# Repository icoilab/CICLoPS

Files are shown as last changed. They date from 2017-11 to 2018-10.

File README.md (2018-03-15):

# CICLoPS Photometry Project
Open source in-vivo fiber photometry for low-light level recordings

# Background
Fiber photometry is a tool used in neuroscience to optically monitor neural correlates of behavior to targeted neuronal populations in the brain. When applied to study neurons genetically-targeted to express optical reporters of local physiological dynamics, the experimentalist gains access to real-time activity of arbitrary neuronal populations during behavioral assays. 

The technology surrounding photometry has matured rapidly, and multiple systems have been reported and several solutions are now commercially available. However, mainstream technologies have limitations, of which poor sensitivity to fluorescence is a notable challenge. This problem is compensated in experiments by increasing the level of input excitation light. However, this causes increased destruction of the fluorescent proteins, which results in a reduction in overall brightness, and largely restricts studies to short-term transients, precluding longer-term and repeated investigations into optically-reported neuronal activity. The [Integrated Circuits and Optical Imaging Laboratory](http://people.ucalgary.ca/~kmurari/index.html) at the University of Calgary developed a high-performance, cost-effective system for deep-brain optical measurements of fluorescence intensity transients in freely-moving animals that achieves excellent Signal-to-noise ratio at extremely low levels of input excitation light. The system is named CICLoPS for **C**ost-effective, ***I**n-Vivo*, **C**ustomizeable, **Lo**w-Power, **P**hotometry **S**ystem.

# Components
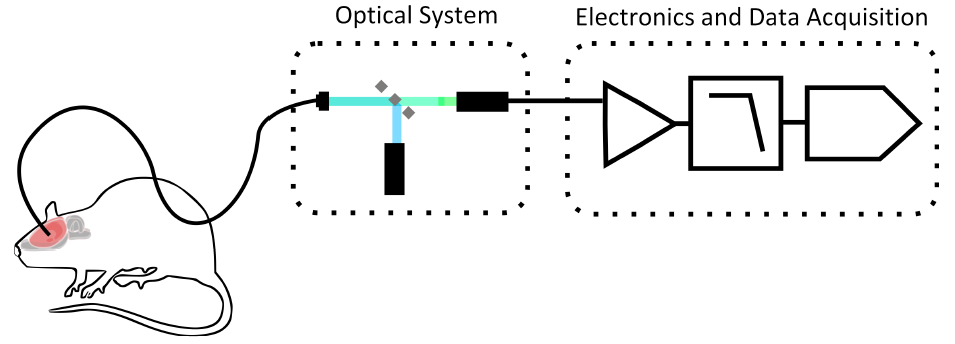
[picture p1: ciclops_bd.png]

CICLoPS is a complete solution for in-vivo fiber photometry, designed specifically to monitor neural activity with low-light levels. The Construction and Assembly Guide for the [core system](../../tree/master/ciclops-core "ciclops-core") refers to source files in the [optical system](../../tree/master/ciclops-core/optics "optics"), [coherent detection hardware](../../tree/master/ciclops-core/electronics "electronics"), and [code for data acquisition](../../tree/master/ciclops-core/acquisition "acquisition"). Instructions on how to achieve [additional functions](../../tree/2x-artifact) are also provided.

# Related Work
This development builds on the prior contributions from several others, listed below.

[1] Grienberger, Christine, et al. "Sound‐evoked network calcium transients in mouse auditory cortex in vivo." The Journal of physiology 590.4 (2012): 899-918.

[2] Cui, Guohong, et al. "Deep brain optical measurements of cell type–specific neural activity in behaving mice." Nature protocols 9.6 (2014): 1213.

[3] Gunaydin, Lisa A., et al. "Natural neural projection dynamics underlying social behavior." Cell 157.7 (2014): 1535-1551.

[4] LeChasseur, Yoan, et al. "A microprobe for parallel optical and electrical recordings from single neurons in vivo." Nature methods 8.4 (2011): 319-325.

[5] Lerner, Talia N., et al. "Intact-brain analyses reveal distinct information carried by SNc dopamine subcircuits." Cell 162.3 (2015): 635-647.

[6] Kim, Christina K., et al. "Simultaneous fast measurement of circuit dynamics at multiple sites across the mammalian brain." Nature 201 (2016): 6.

[7] Pashaie, Ramin, and Ryan Falk. "Single optical fiber probe for fluorescence detection and optogenetic stimulation." IEEE Transactions on Biomedical Engineering 60.2 (2013): 268-280.

[8] Doronina‐Amitonova, Lyubov V., et al. "Fiber‐optic probes for in vivo depth‐resolved neuron‐activity mapping." Journal of biophotonics 3.10‐11 (2010): 660-669.

[9] Guo, Qingchun, et al. "Multi-channel fiber photometry for population neuronal activity recording." Biomedical optics express 6.10 (2015): 3919-3931.

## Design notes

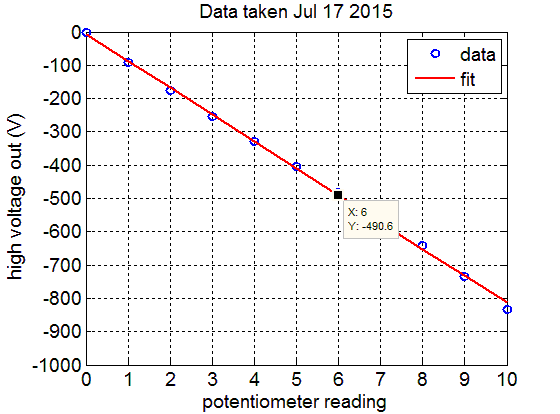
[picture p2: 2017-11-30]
ciclops-core/optics/pmtpsu.bmp

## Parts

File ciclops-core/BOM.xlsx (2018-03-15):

item | part number | manufacturer | description | cost(USD) | Cost (CAD) | Quantity |  | Cost (USD)
Data Acquisition
Data Acquisition Card | USB-6351 | National Instruments | X Series Data Acquisition: 1.25MS/s 16 AI 24 DIO, 2 AO |  | $2385.00 | 1 | $2385.00 | $1834.62
 |  |  |  |  |  |  |  | $0.00
Electronics |  |  |  |  |  |  |  | $0.00
battery clips | 232 | Keystone Electronics |  | $0.60 | $0.78 | 4 | $3.12 | $2.40
LED | LXML-PB02 | Lumileds |  |  | $4.44 | 1 | $4.44 | $3.42
Wire wrap, blue | R-30B-0050 | Jonard Tools |  |  | $10.10 | 1 | $10.10 | $7.77
wire wrap, white | R-30W-0050 | Jonard Tools |  |  | $10.10 | 1 | $10.10 | $7.77
PCB |  |  | as specified by pcb_layout.PcbDoc |  | $60.00 | 1 | $60.00 | $46.15
-12V regulator | MC7912CD2TG | ON Semiconductor |  |  | $0.66 | 1 | $0.66 | $0.51
+12V regulator | MC7812CD2TG | ON Semiconductor |  |  | $0.64 | 1 | $0.64 | $0.49
Multiplier IC | AD633ARZ | Analog Devices | IC MULTIPLIER ANALOG 8-SOIC |  | $12.84 | 1 | $12.84 | $9.88
opamp for TIA | OPA2140AIDR | Texas Instruments | IC OPAMP JFET 11MHZ RRO 8SOIC |  | $5.96 | 2 | $11.92 | $9.17
Headers, 2-pin, male | 61300211121 | Wurth Electronics Inc. | CONN HEADER 2 POS 2.54 |  | $0.13 | 20 | $2.60 | $2.00
Headers, 3-pin, male | 61300311121 | Wurth Electronics Inc. | CONN HEADER 3 POS 2.54 |  | $0.13 | 20 | $2.60 | $2.00
Headers, 2-pin, female receptable | PPPC021LFBN-RC | Sullins Connector Solutions | CONN HEADER FEMALE 2POS .1" GOLD |  | $0.37 | 10 | $3.70 | $2.85
opamp for LED driver | OPA171 | Texas Instruments | IC OPAMP GP 3MHZ RRO SOT23-5 |  | $1.70 | 1 | $1.70 | $1.31
opamp for LIA frontend | AD8065 | Analog Devices | Op Amps SOT23 Hi Perf Hi Spd FET Amp w/ Disable |  | $8.42 | 1 | $8.42 | $6.48
Passive for LIA frontend | HMC1206JT100M | Stackpole Electronics | RES SMD 100M OHM 5% 1/4W 1206 |  | $0.81 | 4 | $3.24 | $2.49
Passive for LIA frontend | RC0603JR-0716KL | Yageo | RES SMD 16K OHM 5% 1/10W 0603 |  | $0.00149 | 20 | $0.03 | $0.02
Passive for LIA frontend | RC0603FR-07270KL | Yageo | RES SMD 270K OHM 1% 1/10W 0603 |  | $0.00192 | 20 | $0.04 | $0.03
Passive for LIA frontend | RC0603FR-07220KL | Yageo | RES SMD 220K OHM 1% 1/10W 0603 |  | $0.00192 | 20 | $0.04 | $0.03
Passive for LIA frontend | RC0603FR-07100KL | Yageo | RES SMD 100K OHM 1% 1/10W 0603 |  | $0.00192 | 20 | $0.04 | $0.03
Passive for LIA frontend | RC0603FR-0757K6L | Yageo | RES SMD 57.6K OHM 1% 1/10W 0603 |  | $0.00192 | 20 | $0.04 | $0.03
Decoupling capacitors | GRM155R61C104KA88J | Murata Electronics North America | CAP CER 0.1UF 16V X5R 0402 |  | $0.00194 | 10 | $0.02 | $0.01
Passive for LIA frontend | UQCFVA0R3BAT2A\500 | AVX Corporation | CAP CER 0.3PF 250V 0805 |  | $1.42 | 4 | $5.68 | $4.37
Passive for LIA frontend | GRM155R61C225KE11D | Murata Electronics North America | CAP CER 2.2UF 16V X5R 0402 |  | $0.19 | 20 | $3.80 | $2.92
Passive for LIA frontend | GRM155R61A394KE15D | Murata Electronics North America | CAP CER 0.39UF 10V X5R 0402 |  | $0.13 | 20 | $2.60 | $2.00
Passive for LIA frontend | C1005X5R1C684K050BC | TDK Corporation | CAP CER 0.68UF 16V X5R 0402 |  | $0.20 | 20 | $4.00 | $3.08
Passive for LIA frontend | GRM155R71H392KA01D | Murata Electronics North America | CAP CER 3900PF 50V X7R 0402 |  | $0.02 | 20 | $0.40 | $0.31
Passive for LIA frontend | GRM155R71H102KA01D | Murata Electronics North America | CAP CER 1000PF 50V X7R 0402 |  | $0.01 | 20 | $0.20 | $0.15
BNC to BNC cable | 115101-02-24.00 | Amphenol RF Division | CABLE BNC/BNC 24" RG-174 |  | $12.61 | 3 | $37.83 | $29.10
Panel Mount Female BNC Connector | 31-221-RFX | Amphenol RF Division | BNC Connector receptable, female socket 50 ohm panel mount solder cup |  | $3.00 | 3 | $9.00 | $6.92
 |  |  |  |  |  |  |  | $0.00
Detector & High Voltage Power Supply |  |  |  |  |  |  |  | $0.00
Photomultiplier tube | H10771-40P | Hamamatsu | Photomultiplier tube | $2500.00 | $3250.00 | 1 | $3250.00 | $2500.00
High voltage supply for PMT | C4900-01 | Hamamatsu | High voltage power supply module | $200.00 | $260.00 | 1 | $260.00 | $200.00
+15V Wall adapter for high voltage supply | WSU150-0560 | Triad Magnetics | 15V 8.4W AC/DC External Wall Mount Adapter Fixed Blade Input |  | $12.63 | 1 | $12.63 | $9.72
2" x 4" Aluminum tubing for enclosure, 2" length | 6546K42 | McMaster Carr | 6061 Aluminum Rectangular Tube, 1/8" Wall Thickness, 2" High x 4" Wide |  | $10.68 | 1 | $10.68 | $8.22
316 Stainless Steel Shim Stock, 8" x 12" Sheet, 0.002" Thick | 2317K52 | McMaster Carr | 316 Stainless Steel Shim Stock |  | $7.87 | 1 | $7.87 | $6.05
Set screws for enclosure | 91772A057 | McMaster Carr | 18-8 Stainless Steel Phillips Rounded Head Screw, 0-80 Thread Size, 3/8" Long |  | $7.87 | 1 | $7.87 | $6.05
Spacer for mounting electronics | 91115A509 | McMaster Carr | Female Threaded Hex Standoff, 18-8 Stainless Steel, 3/16" Hex, 3/8" Long, 4-40 Thread |  | $2.14 | 2 | $4.28 | $3.29
Spacer set screw | 91770A108 | McMaster Carr | 18-8 Stainless Steel Extra Wd Phillips Rounded Head Screws, Passivated, 4-40 Thread Size, 3/8" Long |  | $4.35 | 1 | $4.35 | $3.35
low drop out regulator for PMT PSU | LM7812CT | ON Semiconductor | IC REG LDO 12V 1A TO220-3 |  | $1.54 | 1 | $1.54 | $1.18
Free-hanging male BNC Connector | 031-4321 | Amphenol RF Division | BNC Connector Plug, Male Pin 50 Ohm Free Hanging (In-Line) Crimp |  | $14.30 | 1 | $14.30 | $11.00
Panel Mount male BNC Connector | 112420 | Amphenol RF Division | BNC Connector Receptacle, Male Pin 50 Ohm Panel Mount Solder Cup |  | $6.00 | 1 | $6.00 | $4.62
Free-hanging female BNC Connector | 031-317 | Amphenol RF Division | BNC Connector Jack, Female Socket 50 Ohm Free Hanging (In-Line) Crimp |  | $22.00 | 1 | $22.00 | $16.92
high voltage cap 1 for PMT PSU | ECA-1JHG470 | Panasonic Electronic Components | CAP ALUM 47UF 63V 20% RADIAL |  | $0.34 | 1 | $0.34 | $0.26
high voltage cap 2 for PMT PSU | 940C20P22K-F | Cornell Dubilier Electronics (CDE) | CAP FILM 0.22UF 10% 2KVDC AXIAL |  | $6.15 | 1 | $6.15 | $4.73
120VAC to 15VDC converter | WSU150-0560 | Triad Magnetics | AC/DC WALL MOUNT ADAPTER 15V 8W |  | $7.75 | 1 | $7.75 | $5.96
power connector for switching xfmr | PJ-005A | CUI Inc. | CONN PWR JACK 2X5.5MM SOLDER |  | $2.11 | 1 | $2.11 | $1.62
copper stripboard | 8016-1 | Vector Electronics | PC BOARD FR4 1-SIDE PPH 6.0X6.0 |  | $15.53 | 1 | $15.53 | $11.95
potentiometer for PMT PSU output control | H-516-6A | Bourns Inc | DIAL COUNTING 0-15 TURNS |  | $9.35 | 1 | $9.35 | $7.19
 |  |  |  |  |  |  |  | $0.00
Optics |  |  |  |  |  |  |  | $0.00
blackout material | BK5 | Thorlabs | blackout frabric | $48.50 | $63.05 | 1 | $63.05 | $48.50
epoxy | Plastic Bonder | JB Weld | epoxy to attach PMT onto shutter | $9.49 | $12.34 | 1 | $12.34 | $9.49
shutter | SM1SH1 | Thorlabs | Threaded Manual Beam Shutter | $56.50 | $73.45 | 1 | $73.45 | $56.50
translation mount | LM1XY | Thorlabs | Translating Lens Mount for Ø1" Optics | $144.00 | $187.20 | 1 | $187.20 | $144.00
lens tube coupler | SM1T2 | Thorlabs | Coupler, External Threads, 0.5" Long | $19.90 | $25.87 | 1 | $25.87 | $19.90
reflective neutral density filter | ND504B | Thorlabs | Unmounted Reflective Ø1/2" ND Filter, Optical Density: 0.4 | $25.50 | $33.15 | 1 | $33.15 | $25.50
lens tube | SM1L30 | Thorlabs | SM1 Lens Tube, 3.00" Thread Depth, One Retaining Ring Included | $26.50 | $34.45 | 2 | $68.90 | $53.00
lens tube | SM1L10 | Thorlabs | SM1 Lens Tube, 1.50" Thread Depth, One Retaining Ring Included | $14.25 | $18.53 | 4 | $74.10 | $57.00
lens tube | SM1L05 | Thorlabs | SM1 Lens Tube, 0.50" Thread Depth, One Retaining Ring Included | $12.59 | $16.37 | 1 | $16.37 | $12.59
Cover plate for filter cube | B1C | Thorlabs | Blank Cover Plate | $18.40 | $23.92 | 1 | $23.92 | $18.40
Cage cube platform | B3C | Thorlabs | Fixed Cage Cube Platform | $24.40 | $31.72 | 1 | $31.72 | $24.40
Mount for dichroic filter | FFM1 | Thorlabs | 30-mm Cage-Compatible Rectangular Filter Mount | $57.25 | $74.42 | 1 | $74.42 | $57.25
Cage cube for filter and lens tube mounting | C4W | Thorlabs | 30-mm cage cube | $59.25 | $77.03 | 1 | $77.03 | $59.25
Adapter for 19.5 mm lens | SM1A6T | Thorlabs | Adapter with External SM1 Threads and Internal SM05 Threads, 0.40" Thick | $20.20 | $26.26 | 1 | $26.26 | $20.20
Light source collimation lens | AC127-019-A | Thorlabs | f=19.0 mm, Ø1/2" Achromatic Doublet, ARC: 400-700 nm | $51.00 | $66.30 | 1 | $66.30 | $51.00
Coupling lens for optical fiber tether | F240FC-532 | Thorlabs | 543 nm, f = 7.86 mm, NA=0.51 FC/PC Fiber Collimation Pkg | $148.00 | $192.40 | 1 | $192.40 | $148.00
Focusing lens for detection | AC254-040-A | Thorlabs | f=40.0 mm, Ø1" Achromatic Doublet, ARC: 400-700 nm | $75.00 | $97.50 | 1 | $97.50 | $75.00
dichroic mirror | FF01-504/12-25 | Semrock | 495 nm long pass dichroic mirror | $300.00 | $390.00 | 1 | $390.00 | $300.00
excitation filter | ET470/40X | Chroma Technologies | 470/40 nm excitation filter | $325.00 | $422.50 | 1 | $422.50 | $325.00
emission filter | FF01-515/30 | Semrock | 515/30 nm emission filter | $355.00 | $461.50 | 1 | $461.50 | $355.00
post for cage cube | TR3 | Thorlabs | Ø1/2" Optical Post, SS, 8-32 Setscrew, 1/4"-20 Tap, L = 4" | $6.00 | $7.80 | 1 | $7.80 | $6.00
post holder and base | UPH4 | Thorlabs | Ø1/2" Universal Post Holder, Spring-Loaded Locking Thumbscrew, L = 4" | $33.50 | $43.55 | 1 | $43.55 | $33.50
Optical Breadboard | MB1012 | Thorlabs | Aluminum Breadboard 10" x 12" x 1/2", 1/4"-20 Taps | $132.00 | $171.60 | 1 | $171.60 | $132.00
optical fiber | MFP_400/440/900-0.53_3m_FC-MF2.5 | Doric Lenses | Optical fiber patchcord |  | $70.00 | 1 | $70.00 | $53.85
 |  |  |  |  |  | Total Data Acquisition | $2385.00 | $1834.62
 |  |  |  |  |  | Total Electronics | $199.79 | $153.69
 |  |  |  |  |  | Total Optics | $2710.92 | $2085.33
 |  |  |  |  |  | Total Detector | $3642.75 | $2802.12
 |  |  |  |  |  | Total | $8938.47 | $6875.74
 |  |  |  |  |  |  | CAD | USD

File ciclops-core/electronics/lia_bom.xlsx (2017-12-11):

Comment | Description | Value | Designator | Footprint | Quantity
RC0603JR-0716KL | Resistor | 15.9K | r1t, r2t | J1-0603 | 2
RC0603FR-07270KL | Resistor | 270K | R1x | J1-0603 | 1
RC0603FR-07220KL | Resistor | 220K | R2x | J1-0603 | 1
RC0603FR-07100KL | Resistor | 100K | rled | J1-0603 | 1
RC0603FR-0757K6L | Resistor | 57.6K | R1y, R2y | J1-0603 | 2
OPA2140 | dual channel JFET op amp |  | LPF, TIA | D008_L | 2
OPA171 | Single supply opamp SOT 553 |  | LED driver | S5 | 1
(FUTURE USE - LEAVE OPEN) | Ceramic Chip Capacitor - Standard | 0 | ctia | 1206 | 1
MC7912 | -12 V LDO regulator |  | NREG | D2PAK_L | 1
MC78M12 | +12 V LDO regulator |  | PREG | D2PAK_L | 1
HMC1206JT100M | Resistor | 100meg | rtia | 1206 | 1
Header 3 | Header, 3-Pin |  | BATT, SUPPLY | HDR1X3 | 2
Header 2 | Header, 2-Pin |  | demod, led out, mod, pmt in, sig out, vtia, x cntrl | HDR1X2 | 7
GRM155R71H392KA01D | Ceramic Chip Capacitor - Standard | 3.9n | c1t, c1x, c3x, c5x, c7x, c9x, c11x, c13x, c15x | 0402 | 9
GRM155R71H102KA01D | Ceramic Chip Capacitor - Standard | 1n | c2t, c2x, c4x, c6x, c8x, c10x, c12x, c14x, c16x | 0402 | 9
GRM155R61C225KE11D | Ceramic Chip Capacitor - Standard | 2.2uF | C1, C2, C3, C4 | 0402 | 4
GRM155R61C104KA88J | Ceramic Chip Capacitor - Standard | 0.1u | Csx, Csy | 0402 | 2
GRM155R61A394KE15D | Ceramic Chip Capacitor - Standard | .39u | Cfx | 0402 | 1
C1005X5R1C684K050BC | Ceramic Chip Capacitor - Standard | .68u | Cfy | 0402 | 1
(FUTURE USE - LEAVE OPEN) | NPN Bipolar Transistor |  | Q1 | SOT-23B_N | 1
AD633 | Analog multiplier |  | MULT | D008_L | 1

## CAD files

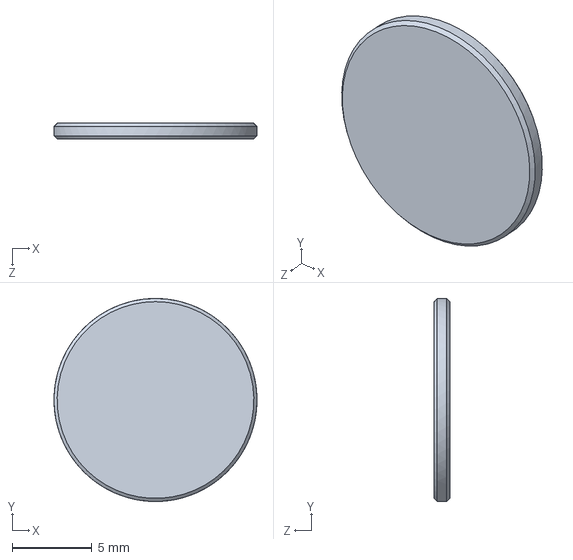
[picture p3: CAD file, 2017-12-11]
ciclops-core/optics/optomechanics/ND504B-Solidworks.sldprt
12.7 x 12.7 x 1.01 mm

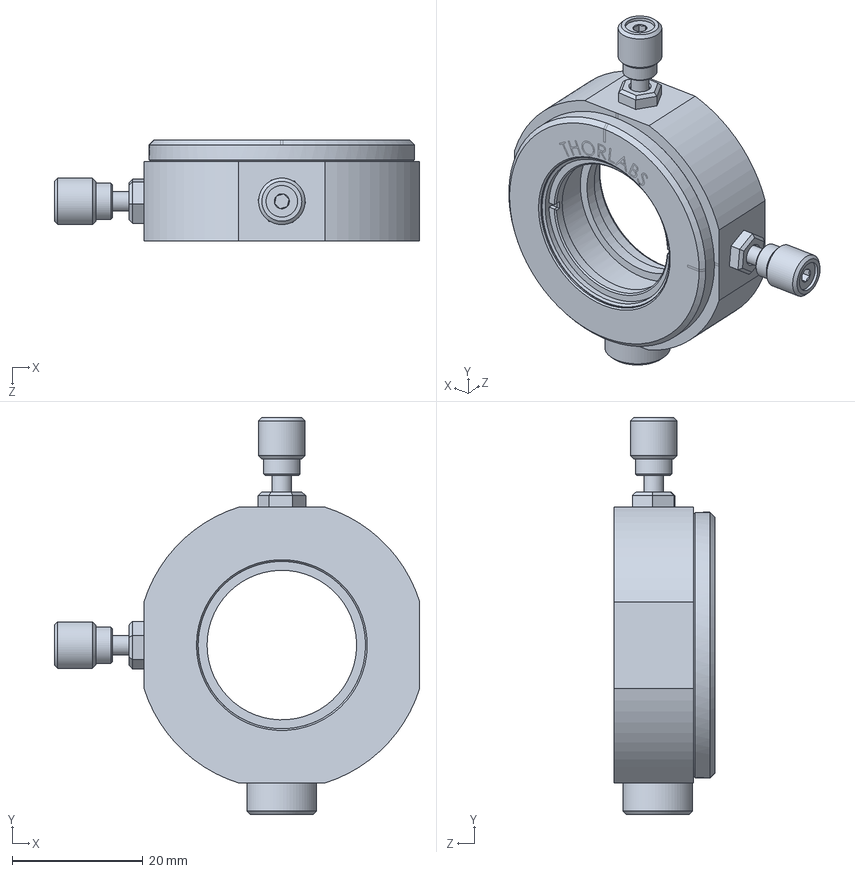
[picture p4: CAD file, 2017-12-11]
ciclops-core/optics/optomechanics/LM1XY-Solidworks.sldprt
55.9 x 60.7 x 15.5 mm

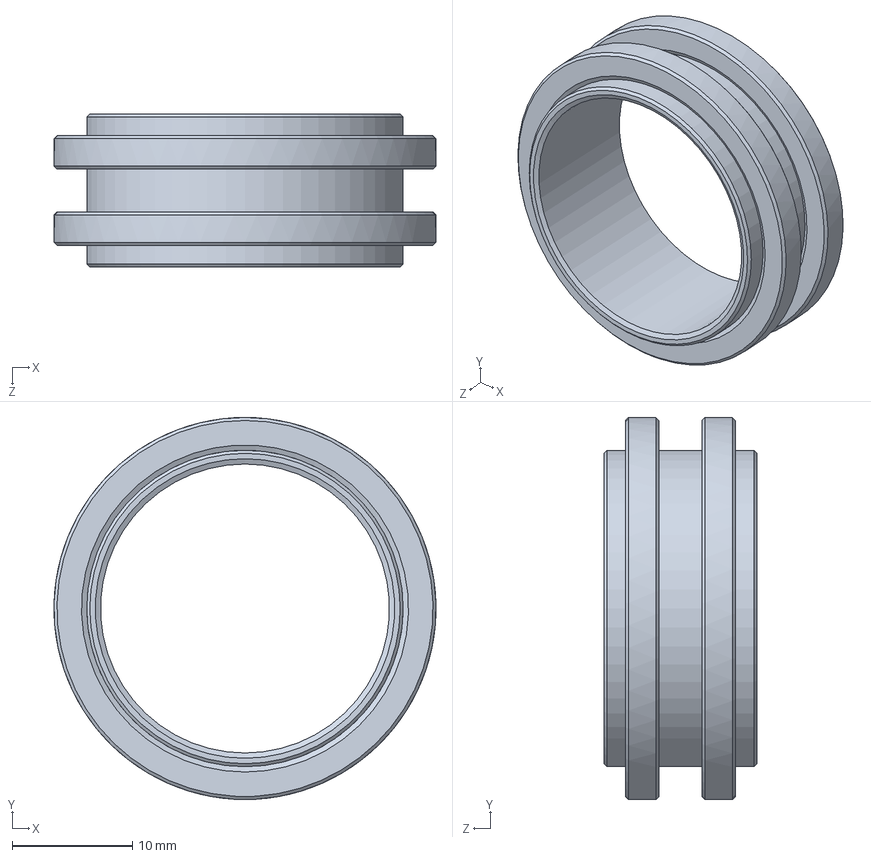
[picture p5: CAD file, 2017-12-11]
ciclops-core/optics/optomechanics/SM1T2-Solidworks.sldprt
31.7 x 31.8 x 12.7 mm

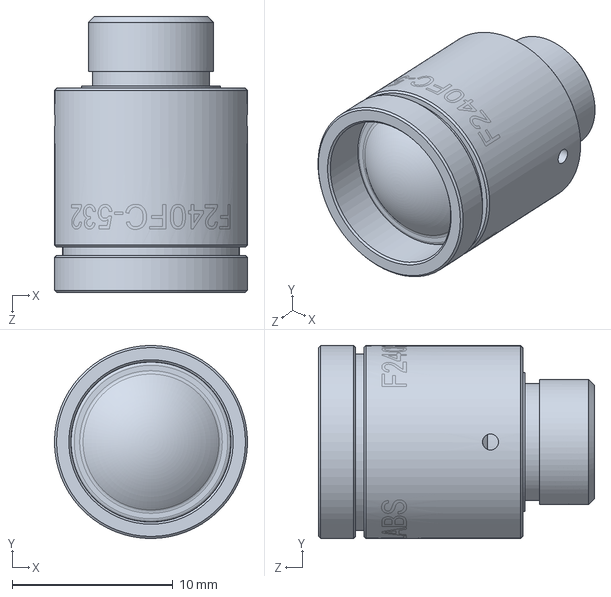
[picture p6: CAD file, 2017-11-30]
ciclops-core/optics/optomechanics/F240FC-532-Solidworks.sldprt
12.0 x 12.0 x 17.2 mm

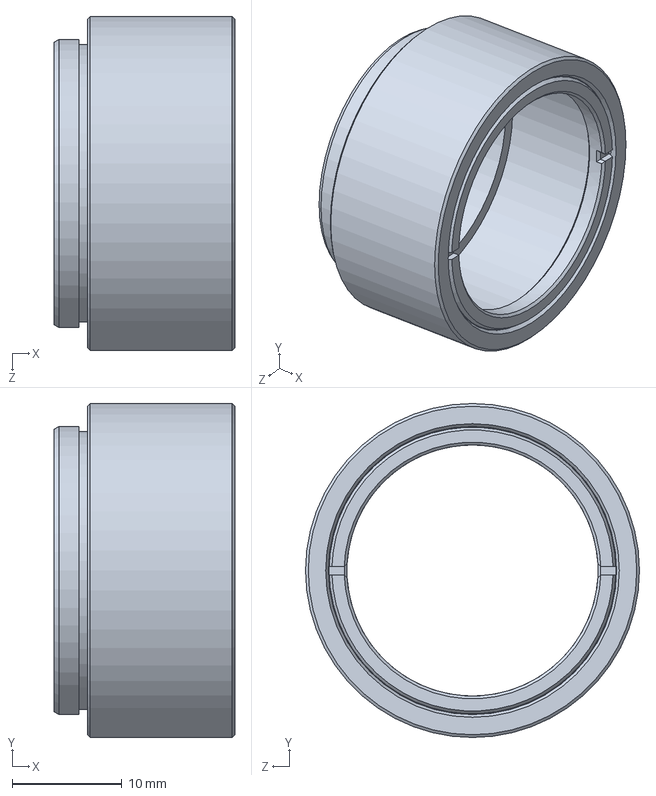
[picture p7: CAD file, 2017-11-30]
ciclops-core/optics/optomechanics/SM1L05-Solidworks.sldprt
16.5 x 30.5 x 30.5 mm

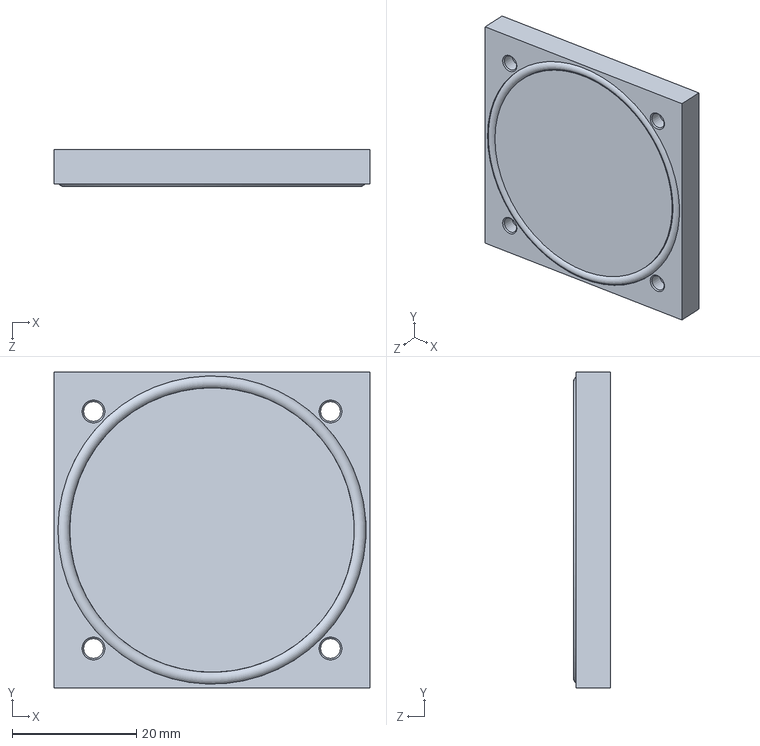
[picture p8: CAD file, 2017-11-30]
ciclops-core/optics/optomechanics/B1C-Solidworks.sldprt
50.8 x 50.8 x 5.97 mm

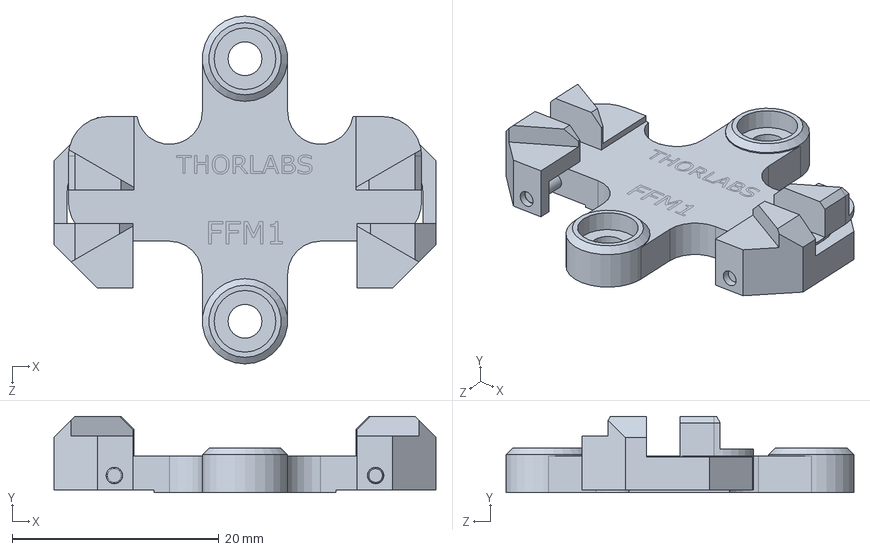
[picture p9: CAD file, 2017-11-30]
ciclops-core/optics/optomechanics/FFM1-Solidworks.sldprt
37.0 x 7.37 x 33.7 mm

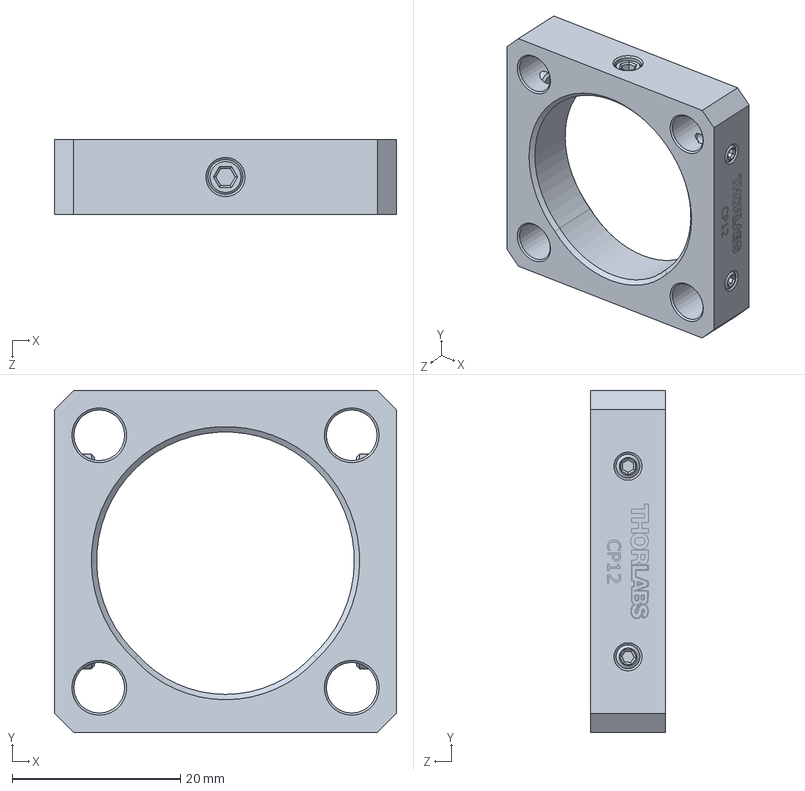
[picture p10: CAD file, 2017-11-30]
ciclops-core/optics/optomechanics/CP12-Solidworks.sldprt
40.6 x 40.6 x 8.89 mm

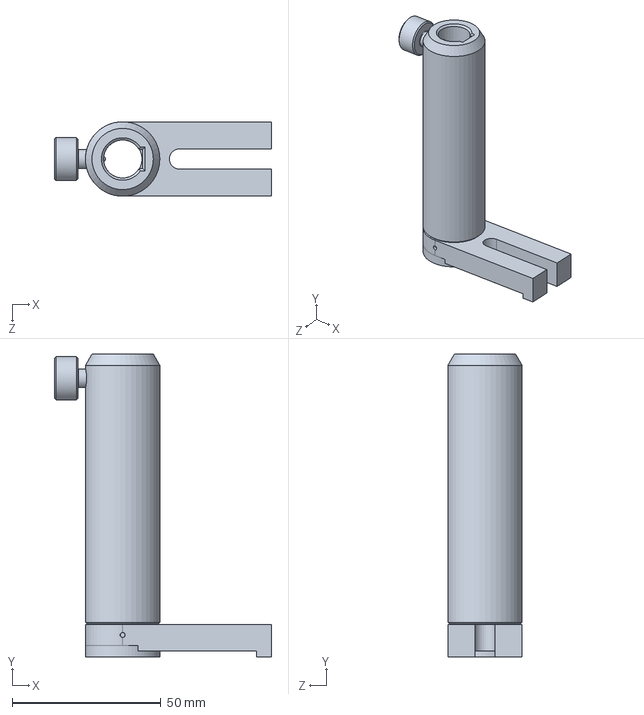
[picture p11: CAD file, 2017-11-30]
ciclops-core/optics/optomechanics/UPH4-Solidworks.sldprt
72.9 x 101.7 x 25.0 mm

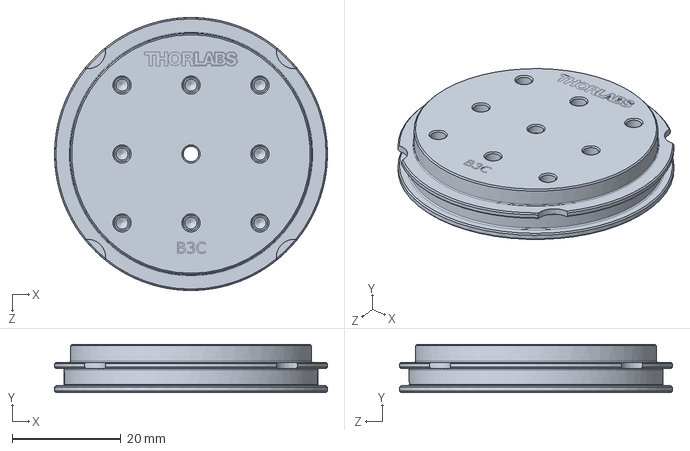
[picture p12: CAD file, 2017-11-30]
ciclops-core/optics/optomechanics/B3C-Solidworks.sldprt
50.3 x 8.89 x 50.3 mm

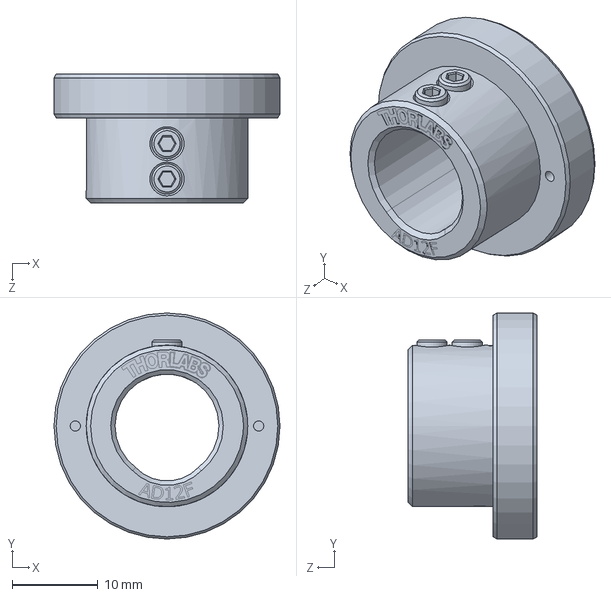
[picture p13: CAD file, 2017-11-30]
ciclops-core/optics/optomechanics/AD12F-Solidworks.sldprt
26.3 x 26.3 x 15.0 mm

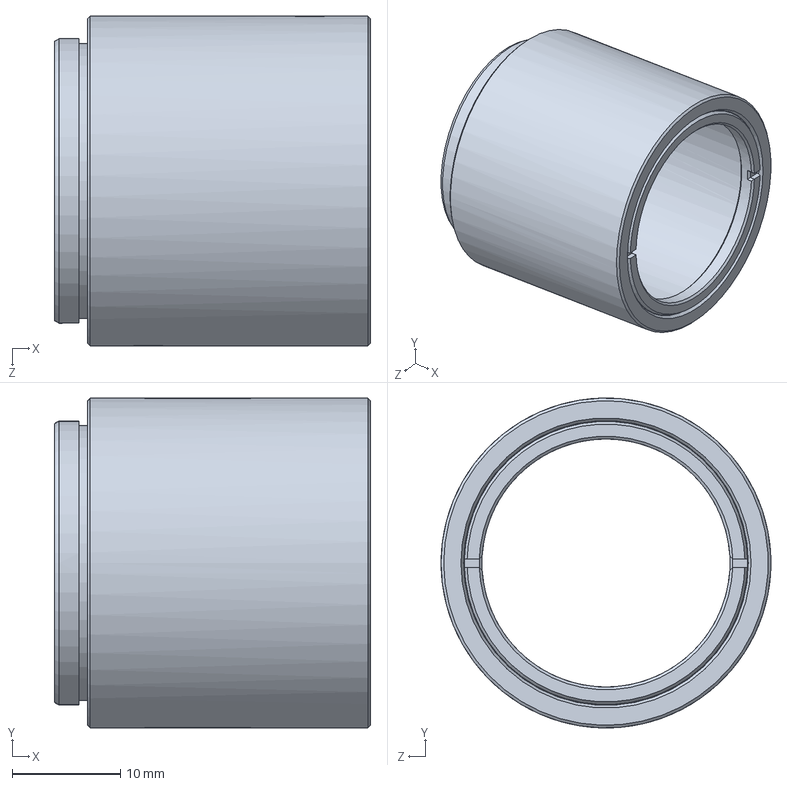
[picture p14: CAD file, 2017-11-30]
ciclops-core/optics/optomechanics/SM1L10-Solidworks.sldprt
29.2 x 30.5 x 30.5 mm

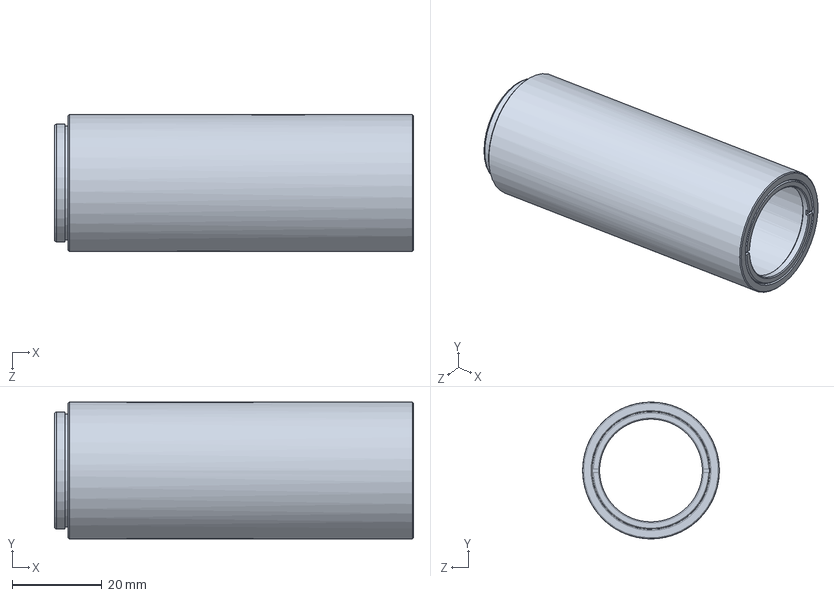
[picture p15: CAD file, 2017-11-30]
ciclops-core/optics/optomechanics/SM1L30-Solidworks.sldprt
80.0 x 30.5 x 30.5 mm

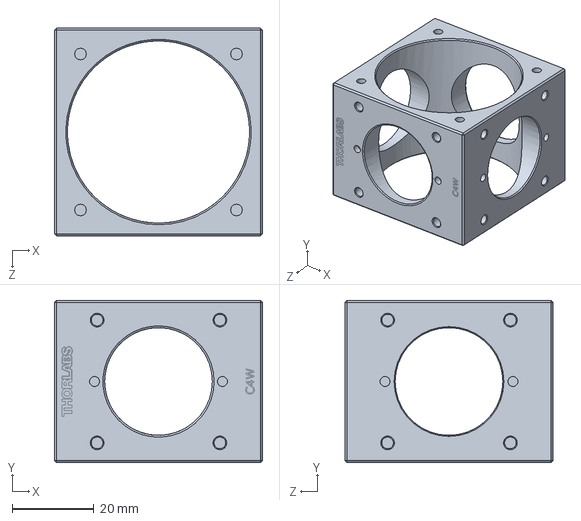
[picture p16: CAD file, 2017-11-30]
ciclops-core/optics/optomechanics/C4W-Solidworks.sldprt
50.8 x 39.6 x 50.8 mm

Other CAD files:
ciclops-core/optics/optomechanics/AC127-019-A-Solidworks.sldprt
ciclops-core/optics/optomechanics/AC254-040-A-Solidworks.sldprt
ciclops-core/optics/optomechanics/TR3-Solidworks.sldprt
ciclops-core/optics/optomechanics/SM1A6T-Solidworks.sldprt
ciclops-core/optics/optomechanics/SM1CP2-Solidworks.sldprt
ciclops-core/optics/optomechanics/SM1SH1-Solidworks.sldprt

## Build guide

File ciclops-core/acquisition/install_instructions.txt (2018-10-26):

Installation instructions for CICLoPS data acquisition API

toolchain
Allegro 4.2 (included in this folder)

NI-DAQmx driver: 
https://www.ni.com/nisearch/app/main/p/bot/no/ap/tech/lang/en/pg/1/sn/catnav:du,n8:3478.41.181.5495,ssnav:ndr/

Microsoft Visual C++ 2010 Express:
https://www.microsoft.com/en-ca/download/details.aspx?id=5555

To install allegro: 
copy bin to MS Install Directory > VC > bin
copy lib to MS Install Directory > VC > lib
copy include to MS Install Directory > VC > include

tips and troubleshooting:
Show file extensions by changing your 'File and Folder Properties'
Compiled with NI-DAQmx 18.5
Check Visual Studio Project Configuration Properties
- VC++
	- Include Directories: <National Instruments Install Path>\NI-DAQ\DAQmx ANSI C Dev\include
	- Library Directories: <National Instruments Install Path>\NI-DAQ\DAQmx ANSI C Dev\lib\msvc
- C\C++
	- General
		- Warning Level: Level 3 (/W3)
	- Optimization
		- Optimization: Disabled
- Linker
	- General
		- Additional Library Directories
	- Input
		- alld.lib; nidaqmx.lib
	- Debugging: YES (/DEBUG)

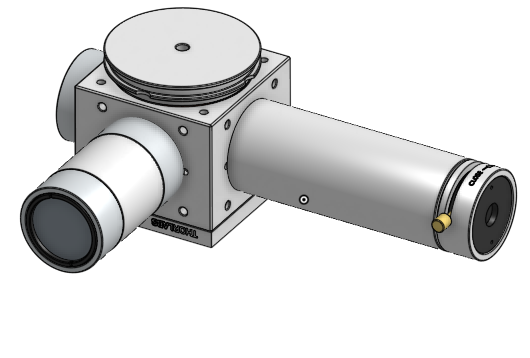
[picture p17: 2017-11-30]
ciclops-core/optics/optics_assembly_sketch.png

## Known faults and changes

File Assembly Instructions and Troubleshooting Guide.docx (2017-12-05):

Assembly Instructions and Troubleshooting Guide

1. Overview

This document provides instructions on how to build the open-source CICLoPS photometry system with explicit reference to the appropriate design files provided. The subassemblies are largely independent of other subassemblies; meaning that they can be developed and tested in parallel if necessary, with a few exceptions. The entire system can be built and tested in 40 hours of work, requiring minimal experience in optical assembly or electronics.

Throughout this document, the following symbols are used:

Symbol | Meaning

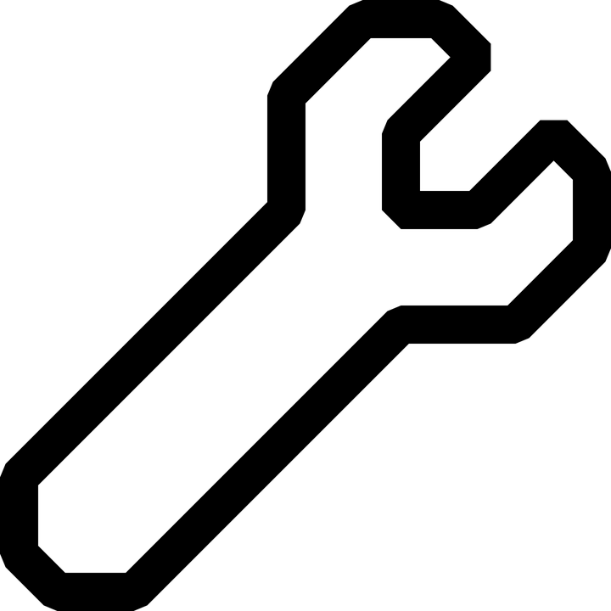
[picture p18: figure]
Free vector graphic: Wrench, Hardware, Tool, Workshop - Free Image ...

| tools needed to complete the subassembly in a given section

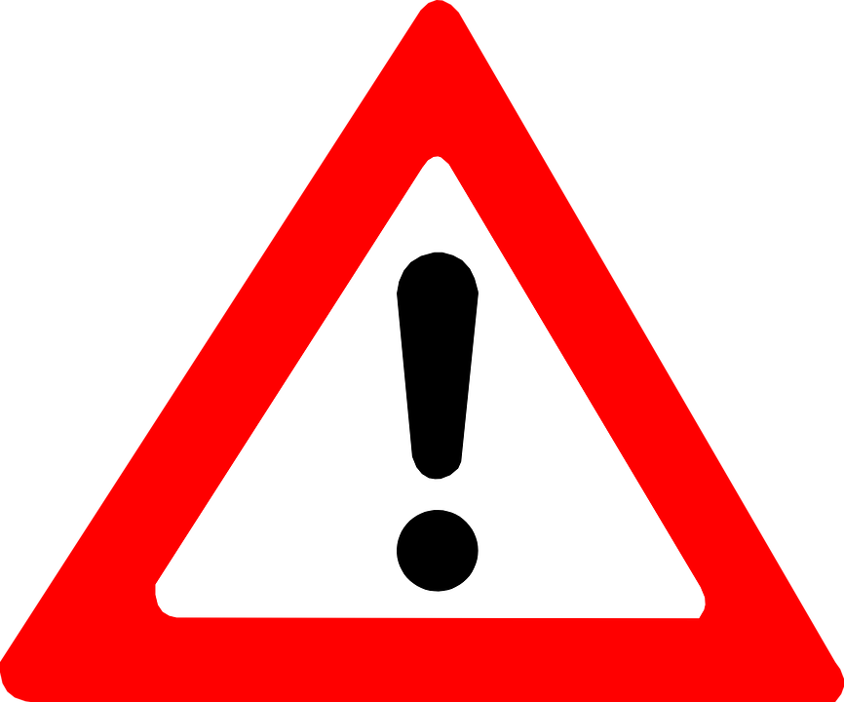
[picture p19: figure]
Free vector graphic: Attention, Warning - Free Image on Pixabay ...

| common problems and causes
| verify that the subassembly is working properly before moving on

2. Subassembly 1: Optical system

The major components of the optical system are the excitation light source, the PMT detector, the optical tether, and the dichroic mirror. A light-tight cage cube system with lens tubes houses collimating, coupling, and focusing lenses while isolating the system from stray light. The time to build the system is approximately 8 hours.

Tools needed

Drill press

Alan key 1/16 ”

SPW602 spanner

½” spanner

Terminal block screwdriver

Current source

Optical Power Meter (PM-100 USB)

White light source

Oscilloscope

Soldering iron

Multimeter

Computer

  a. LED Light Source

The light source is based off of a simple surface mount LED (LXML-PB02, Lumileds). To make this part, first fabricate the LED plate by cutting a 1”-diameter hole into perforated prototyping board, using a drill press and a 1” hole saw. Cut 2- 12” lengths of wire wrap (R-30B-0050 (blue) and R-30W-0050 (white), Jonard Tools), stripping ⅛-inch from the tips. Solder one wire to each of the LED pads as shown. Twist the wire wraps together. The LED may now be powered with either a continuous or modulated current source.

  b. PMT Detector

The PMT (H10771, Hamamatsu) transduces light incident on its photocathode into an electrical current. It will be interfaced directly with the optomechanics to collect photons emitted from the fluorescent sample. The two coaxial cable leads are for high-voltage negative power supply and the output current. This section describes the assembly of the high voltage power supply module.

Design Notes: The design is based of the application in the C4900 datasheet. A voltage divider resistor network prohibits the controlling voltage to exceed ~3.3 V, limiting the high voltage output to a maximum of ~830 V. This is within the safe operating region for the selected PMT.

First, make the enclosure according to hvsupply_enc.dae. We recommend a 2” length of 2”x 2” aluminum tubing (6546K42, McMaster Carr) and sheet aluminum to cover the open ends, using 3/8” set screws to secure the end plates.

Next, make the controllable power supply circuit for the C4900 high voltage power supply from Hamamatsu. and is provided by hvsupply_schem.SchDoc. It is implemented on an 1.8” x 3.8” section of perforated circuit board. Leave approximately 3” of stranded wire for each of the VIN and HVOUT leads for soldering to the BNC and jack plug connectors on the enclosure. Position the rotary potentiometer near its knob’s hole in the enclosure. We recommend providing longer leads for its terminals for ease of positioning.

[insert annotated figures here of built power supply circuit and enclosure]

Hamamatsu power supply

The high voltage output should vary linearly with the number of turns on the potentiometer, at a rate of ~90V per turn. Use a voltage divider circuit to read HVOUT with a conventional multimeter without surpassing its maximum operating range.

  c. Optomechanics

The optomechanics may be thought of as having an excitation input arm, a fiber tether output arm, and a detector arm that converge on a single cage cube (C4W, Thorlabs). The excitation beam is launched into the system via a modulated LED and collimation lens. This beam is then reflected into the optical fiber tether output by the dichroic filter (T495LPXRU, Chroma Technologies). After interacting with the sample, a mix of reflected excitation and fluorescent photons travel back to the system via the optical tether, and are separated at the dichroic mirror. In the detection arm, the beam’s spectral properties are narrowed again by the emission filter (ET470/40X, Chroma Technologies) and then focused onto the PMT detector by the focusing lens (AC254-040-A, Thorlabs).

The accurate model of the optical system (optical_system_assembly.dae) contains exact relative positions between components in the optical system. We recommend that the builder first familiarize themselves with this model and ensure they have all parts before getting started. We recommend building outward from that cage cube one ‘arm’ at a time, as explained here. CICLoPS is an Imperial setup and is not compatible with metric optomechanical parts.

Design Notes: The use of the cage system drastically simplifies the task of aligning the beam. The use of lens tubes reduces the amount of stray light that leaks into the optical system.


Excitation input arm

First screw a ring retainer in 0.5” lens tube (SM1L05, Thorlabs) such that it is flush with the optic retention lip. Then place inside the excitation filter (ET470/40x), ensuring that it is oriented properly (the arrow on the side should point towards the retention lip, as this is the direction of the beam). Secure the filter with a second retaining rings (SM1RR, Thorlabs). We recommend using a spanner wrench (SPW602, Thorlabs) to screw the retaining rings into lens tubes, as they enable accurate distance measurements. Screw the excitation filter assembly onto any one of the four 1” tapped holes.

Next, build the collimation assembly. Screw a 0.5” retaining ring (SM05RR) into the into the 1” - 0.5” adapter (SM1A6T, Thorlabs), such that it is flush with the other end of the adapter. Place inside the focusing lens, such that the convex surface touches the retaining ring. Secure the lens with a second retaining ring. Next, use the 1/16” Alan Key to position the adapter within the 1” lens tube (SM1L10, Thorlabs), ensuring the convex surface of the lens faces the retention lip of the lens tube. The distance between the adapter and the mouth of the lens tube should be 10 mm. Use the spanner wrench to check that the adapter itself is positioned 10 mm from the mouth of the lens tube. Fasten the collimation assembly onto the excitation filter assembly.

Finally, build the excitation assembly. Screw a retaining ring approximately 3 mm into the mouth of a 0.5” lens tube (SM1L05, Thorlabs). Place inside the LED plate and secure with a second retaining ring. Fasten the excitation assembly onto the collimation assembly.

Fiber tether output arm

Secure the collimation package (F240FC-532, Thorlabs) into its adapter (AD12F, Thorlabs) with the set screws and the allan key. Screw the adapter all the way into the 0.5” lens tube (SM1L10, Thorlabs) such that it touches the retention lip. Secure in place with a second retaining ring (SM1RR, Thorlabs). Fasten the fiber tether output arm onto the cage cube, 90 degrees to the left of the excitation input arm.

Next, build the dichroic mirror assembly. Pull a gap between the spring-loaded clamping mechanism of the filter mount (FFM1, Thorlabs) and place the dichroic mirror in between, as in Figure xx below, noting the position of the caret. Gently release the clamping mechanism. Next fasten the filter mount onto the cage cube platform (B3C, Thorlabs), and place into one of the 2” untapped holes of the cage cube. Rotate the platform such that the dichroic mirror is at a 45 degree angle to both of the arms, so that light from the excitation is reflected into the output arm. Fasten the FC/PC connected end of the 200 um optical fiber tether (MFP_200/230/900-0.48, Doric Lenses) onto the mating end of the collimation package.

Collimation package keeps turning when attempting to connect FC/PC connector.

Possible cause: Set screws on adapter for collimation package (AD12F, Thorlabs) are missing and/or not tight enough, OR the retaining ring (SM1RR, Thorlabs) was forgotten.

Detection arm

Place the emission filter (ET510/20, Chroma Technologies) all the way into the 3” lens tube (SM1L30, Thorlabs) to the optic retention lip and secure with a retaining ring. Using the spanner wrench, fasten another retaining ring 30.5 mm into the lens tube, and place the focusing lens (AC254-40-A, Thorlabs) adjacent to it, ensuring the convex surface of the lens faces the retention lip of the lens tube. Secure with another retaining ring. The distance between the retaining ring and the mouth of the lens tube should be 23 mm. Use the spanner wrench to check the position. Fasten the shutter (SM1SH1, Thorlabs) and then the PMT onto the detection assembly. Finally, fasten the detection assembly onto the cage cube, into the tapped hole opposite that of the output detection arm. Fasten the end cap (SM1CP2, Thorlabs) on the last tapped hole.

Delivery path alignment

To test for alignment of the beam, supply the LED with 2 mA of continuous current from a current source. Using the optical power meter, check the excitation output of the fiber tether. The dichroic will be at the desired 45 degree angle when the the output is maximized. If the model is built as specified, the system will output xx uW when the LED is supplied with 2 mA of continuous current.

Excitation path alignment

After disconnecting the PMT from the optical system, feed a white light into the output of the optical tether such that it propagates back to the system. The spot at the mouth of the remaining detection arm should be xx mm in size, as pictured below.

References

3. Subassembly 1: Lock-in Amplification Scheme

Tools needed

Soldering iron

Vice

Tweezers

Solder wick

High speed photodiode (like PDA36A)

Optical Power Meter (PM-100 USB)

The model of the LIA enclosure is specified in lia_enc.dae. For the LIA enclosure, we recommend using a 1.625” length of 1.5” x 1.5” ¼”-thick aluminum tubing, and using 1.5”-square sections of aluminum sheet as end plates. Similar to the PMT enclosure, secure the end plates with set screws.

First, populate the fabricated lock-in amplifier PCB (specified in pcb_layout.PcbDoc) as shown in pcb_assembly.pdf. Drill a hole in the pcb, avoiding the traces, to allow for a set screw to separate the PCB from the enclosure. Use 2” lengths of wire wrap to provide signal lines for sig out, mod, and pmt in. Solder these to their respective female BNC connectors (31-221-RFX, Amphenol RF Division) secured to the enclosure.

Lock-in amplifier power supply

Light source modulation

4. Subassembly 3: Software
  a. Data Acquisition

Both modulation/and demodulation and acquisition of analog data are accomplished with the data acquisition card (USB-6351, National Instruments), using its analog output and analog input, respectively. The daq operations are provided by C++ code developed in Microsoft Visual Studio. The v_write solution enables acquisition of analog data, while lockin_amplifier controls the modulation/demodulation scheme. To collect data coherently, start the lockin_amplifier first (open Lock-in Amplifier.sln), and then begin acquiring data (V_Write.sln).

Design notes: The modulated voltage waveform generated by lockin_amplifier and the daq has offset of zero and amplitude of 9.9. This is the maximum amplitude given the daq’s output range. This waveform is fed directly to the op-amp LED driver. The acquisition range on the daq is set to [-1,1], which is good match to the maximum output range of the lock-in amplifier [0,0.5].

lockin_amplifier

The solution generates a terminal window for user input. The user need only accept each of the prompts to begin generating the modulation/demodulation waveforms to the lock-in amplifier hardware.

v_write

The solution generates a terminal window that prompts for user input on filename. After accepting the remaining prompts, the window generates a real-time display of the incoming data, with a 100 sample averaging operation applied. The user can modify this display to zoom in (z, Enter), zoom out (o, Enter), or center the trace (c, Enter) about the cumulative average of the collected samples using keyboard inputs to the terminal. The experiment can be interrupted at any time (q, Enter). The data is stored in the same folder as the solution in binary values sampled at 100 samples per second.

The acquired data from CICLoPS is written in 16-bit binary values. In any given channel, both the time and Custom Matlab script (binary_read.m) are used to convert the data into decimal values. Example in-vivo data is provided to test this code.

References

Hamamatsu Photonics, June 2012. [Online]. Available: https://www.hamamatsu.com/resources/pdf/etd/C4900_TACC1013E.pdf.

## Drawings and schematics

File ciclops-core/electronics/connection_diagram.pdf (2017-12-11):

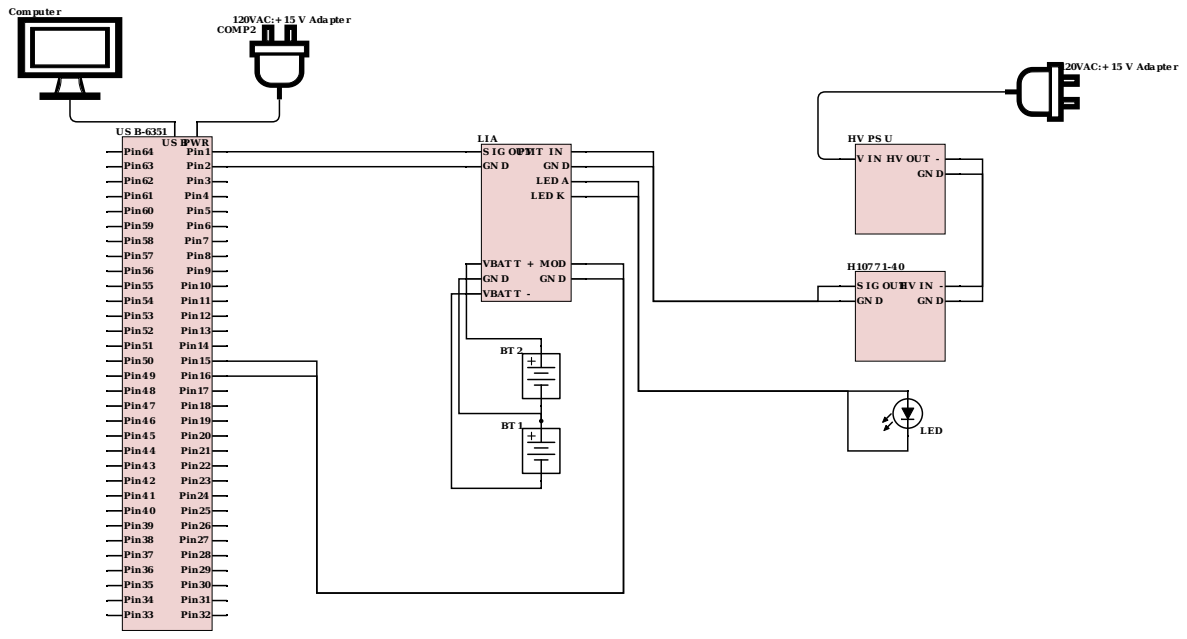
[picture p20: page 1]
pte

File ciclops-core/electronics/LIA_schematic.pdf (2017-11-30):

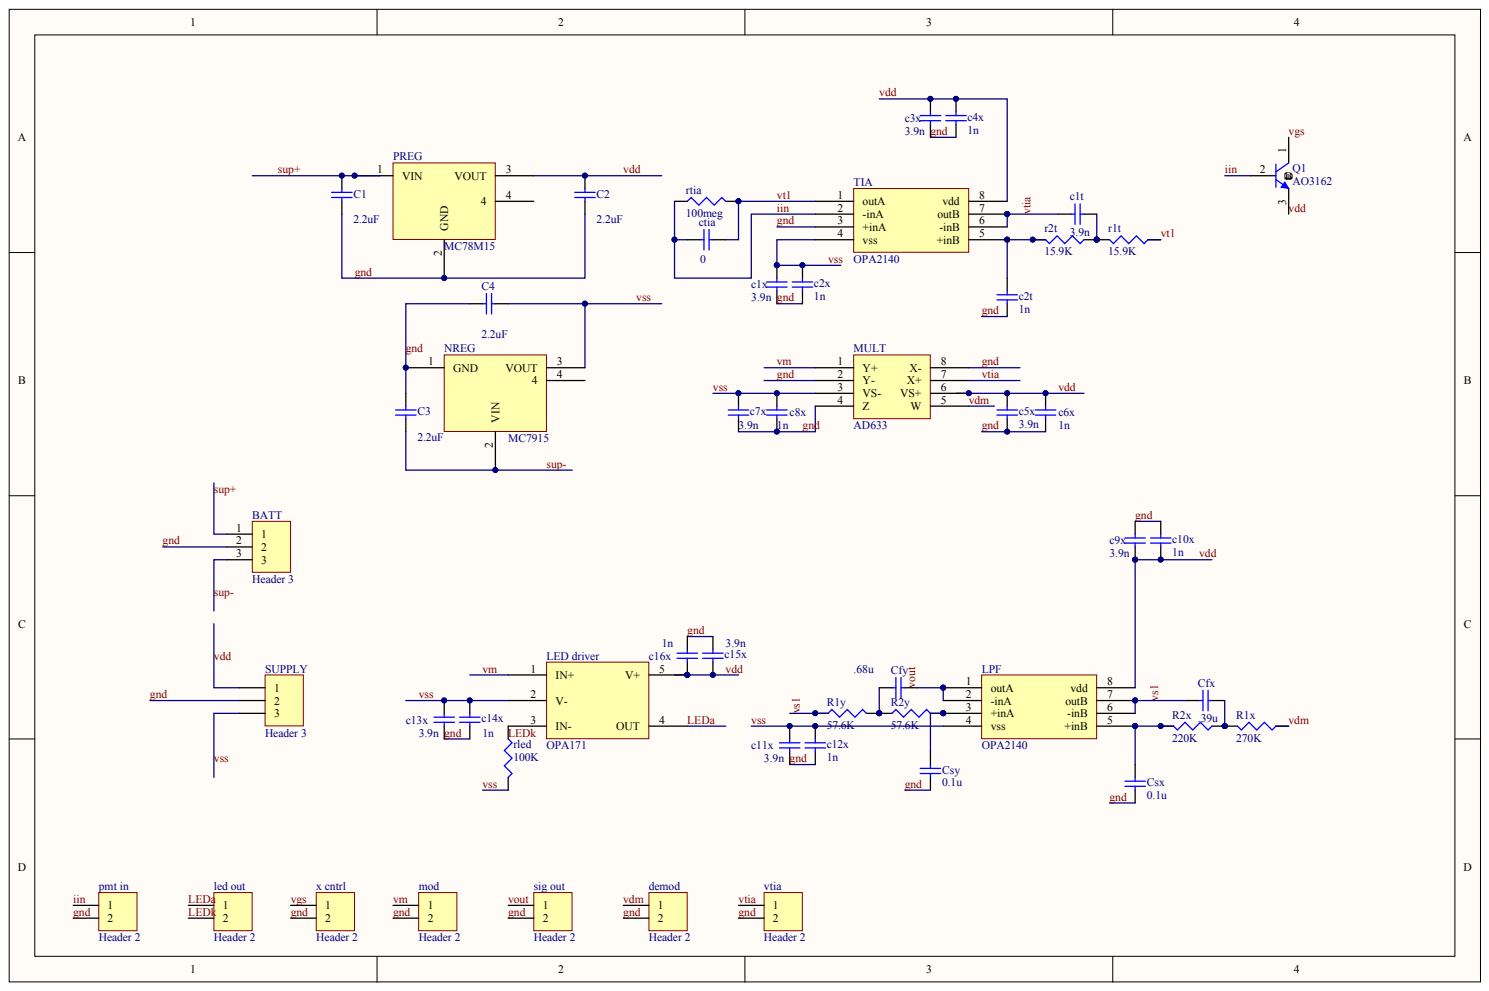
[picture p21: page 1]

2.2uF | MC7915 sup-

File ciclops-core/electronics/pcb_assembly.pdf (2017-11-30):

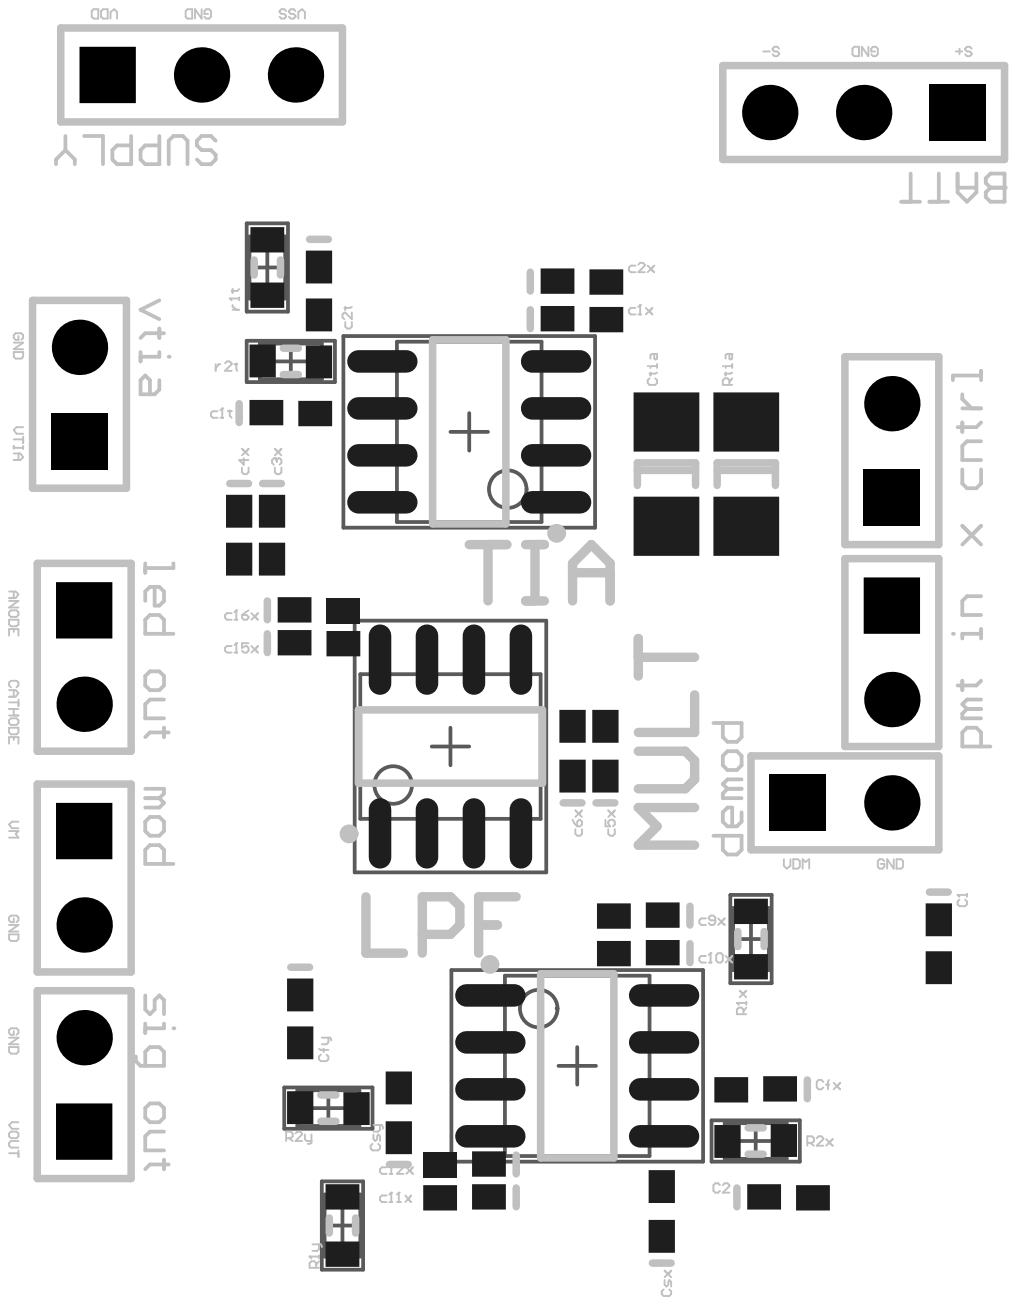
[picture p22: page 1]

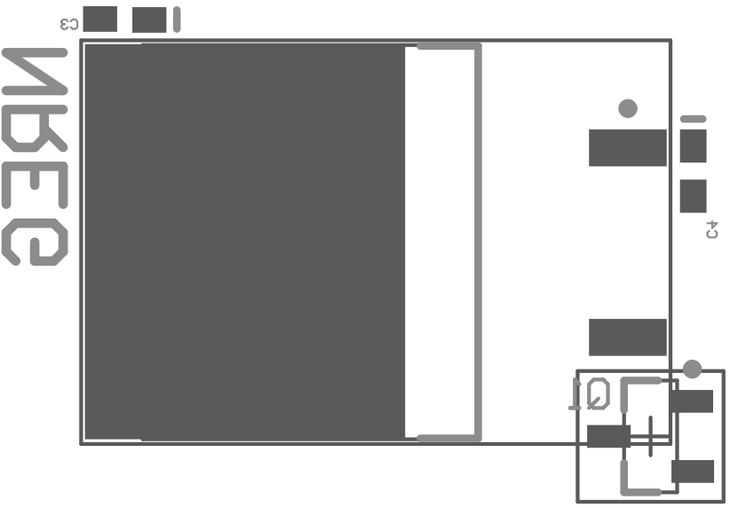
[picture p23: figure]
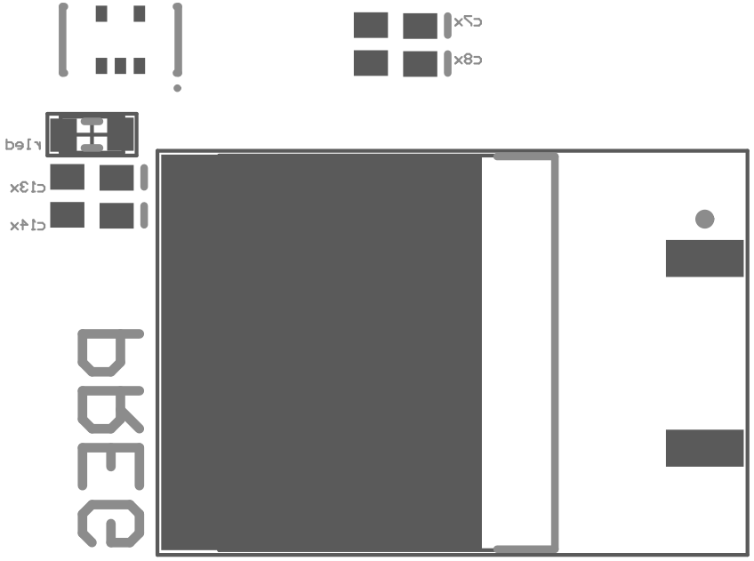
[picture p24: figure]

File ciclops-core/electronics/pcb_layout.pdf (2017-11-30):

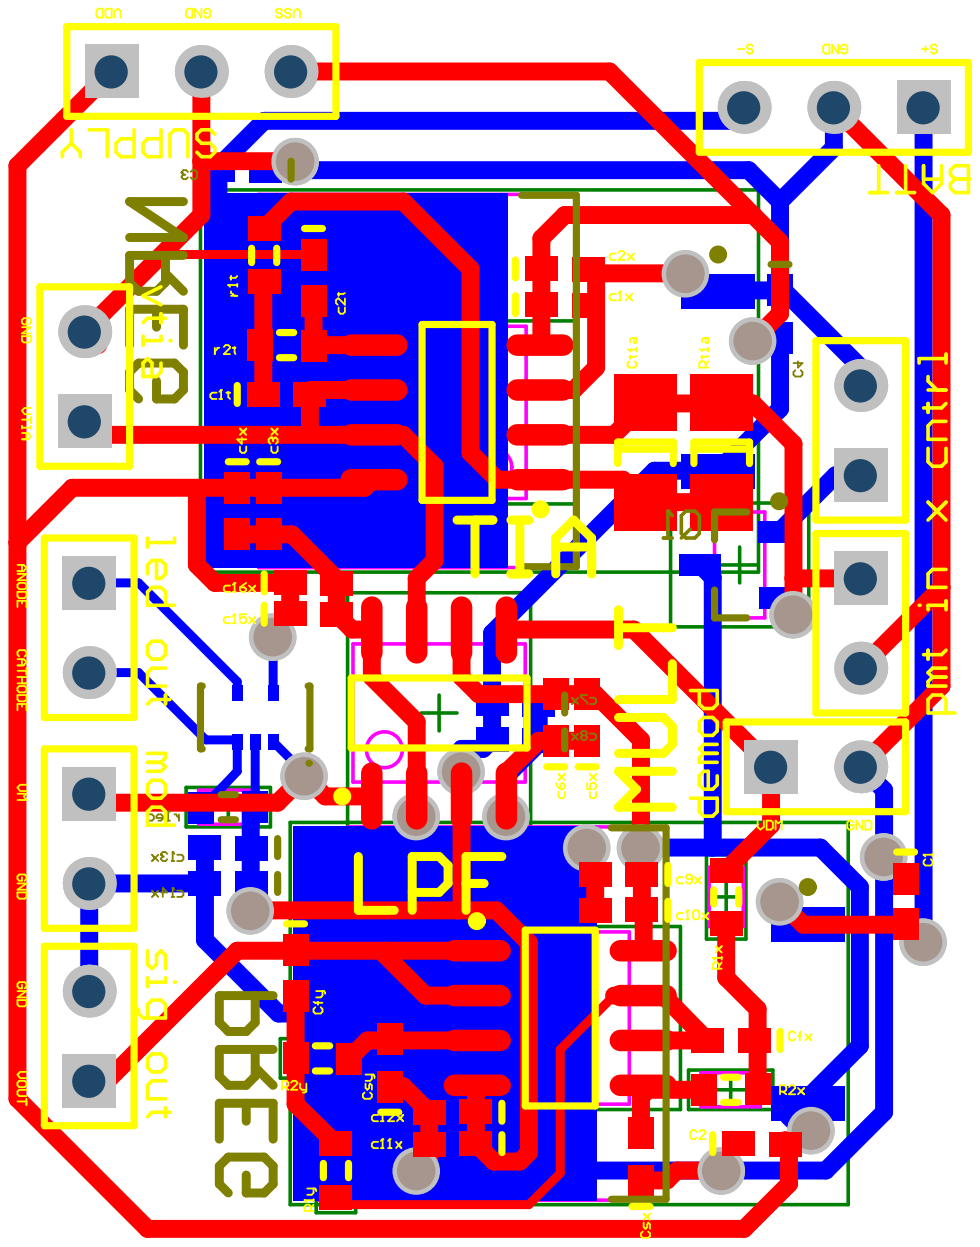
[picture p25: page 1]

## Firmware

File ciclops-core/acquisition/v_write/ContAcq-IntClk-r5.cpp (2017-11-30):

/*********************************************************************

*********************************************************************/
#define ALLEGRO_USE_CONSOLE
#include <stdio.h>
#include <time.h>
#include <math.h>
#include <allegro.h>
#include <NIDAQmx.h>
#include <iostream>
#include <algorithm>
#include <fstream>
#include <sstream>
#include <string>
#include <cstring>

bool inCallBack = false;
bool rescaleRequested = false;
const int NumChannels = 1; 
#define ROW 640
#define COL 692
#define MAX 1
#define MIN -1
#define SR 100
#define SAMPS_PER_CHAN_PER_CALLBACK SR
#define	BUFFER_SIZE 10*SAMPS_PER_CHAN_PER_CALLBACK*NumChannels
#define	EXP_LENGTH 30
	//in minutes		

int displayUpdateNumber = 0;
int screenCycles = 0;
int spacingV = 32;
int spacingH = 48;
int c='\0';
int chan = 0;
int ccol = 0;

BITMAP		*bmp;
PALETTE		pal;

float 		scaleV[8];
//float		scaleH = (COL-2*spacingH)/SR;
float		graphWidth = (ROW-spacingV*(NumChannels+1))/NumChannels;
float		displayedValues[NumChannels][2*EXP_LENGTH*60*SR/SAMPS_PER_CHAN_PER_CALLBACK];
int			col = spacingH+1;
int			zeroPoint[8] = {0,0,0,0,0,0,0,0};
float		cumulativeSum[8] = {0.0,0.0,0.0,0.0,0.0,0.0,0.0,0.0};
float		cumulativeAvg[8] = {0.0,0.0,0.0,0.0,0.0,0.0,0.0,0.0};
double		graphMarkers[NumChannels][5];

void initAllegro();
void initScreen(int channelNumber);
void updateDisplay(int channelNumber);
void redrawTrace(int channelNumber, int ccol);
void centerTrace(int channelNumber);

//void fill(int NumberOfChannels, int value, int &array); // figure out how to do this some other time

using namespace std;
#define DAQmxErrChk(functionCall) if( DAQmxFailed(error=(functionCall)) ) goto Error; else

int32 CVICALLBACK EveryNCallback(TaskHandle taskHandle, int32 everyNsamplesEventType, uInt32 nSamples, void *callbackData);
int32 CVICALLBACK DoneCallback(TaskHandle taskHandle, int32 status, void *callbackData);

	ofstream file;
	string filename;
	FILE * pFile;

int main(){

	int32       error=0;
	char        errBuff[2048]={'\0'};
	TaskHandle  AItaskHandle=0;
	//TaskHandle	AOtaskHandle=0;
	//float64		out[SR];
	float64		zero[1]={0};
	
	for (int i=0;i<NumChannels;i++){
		scaleV[i] = (ROW-spacingV*(NumChannels+1))/(NumChannels*(MAX-MIN));
	}

	int keyval;

	int j = 0;
	//for(;j<SR;j++){
	//	if (j<SR/10)
	//	out[j] = 2;
	//	else if (j<SR)
	//	out[j] = 0;
	//}

	for(;j<NumChannels;j++){
		displayedValues[j][0]=0;
	}


	/*********************************************/
	// DAQmx Configure Code
	/*********************************************/
	//Analog Out
	////DAQmxErrChk (DAQmxCreateTask("",&AOtaskHandle));
	//DAQmxErrChk (DAQmxCreateAOVoltageChan(AOtaskHandle,"Dev1/ao0","",-10,10,DAQmx_Val_Volts,NULL));
	//DAQmxErrChk (DAQmxCfgSampClkTiming(AOtaskHandle,"",SR,DAQmx_Val_Rising,DAQmx_Val_ContSamps,SR));

	const char* physicalChannel = "Dev1/ai1";
		 if (NumChannels == 2) physicalChannel = "Dev1/ai1:2";
	else if (NumChannels == 3) physicalChannel = "Dev1/ai0:2";
	else if (NumChannels == 4) physicalChannel = "Dev1/ai0:3";
	else if (NumChannels == 5) physicalChannel = "Dev1/ai0:4";
	else if (NumChannels == 6) physicalChannel = "Dev1/ai0:5";
 	else if (NumChannels == 7) physicalChannel = "Dev1/ai0:6";
	else if (NumChannels == 8) physicalChannel = "Dev1/ai0:7";

	DAQmxErrChk (DAQmxCreateTask("",&AItaskHandle));
	DAQmxErrChk (DAQmxCreateAIVoltageChan(AItaskHandle,physicalChannel,"",DAQmx_Val_Diff,MIN,MAX,DAQmx_Val_Volts,NULL));

	DAQmxErrChk (DAQmxCfgSampClkTiming(AItaskHandle,"",SR,DAQmx_Val_Rising,DAQmx_Val_ContSamps,BUFFER_SIZE));
	DAQmxErrChk (DAQmxRegisterEveryNSamplesEvent(AItaskHandle,DAQmx_Val_Acquired_Into_Buffer,SAMPS_PER_CHAN_PER_CALLBACK,0,EveryNCallback,NULL));
	DAQmxErrChk (DAQmxRegisterDoneEvent(AItaskHandle,0,DoneCallback,NULL));
	/*********************************************/
	// DAQmx Write Code
	/*********************************************/
	//DAQmxErrChk (DAQmxWriteAnalogF64(AOtaskHandle,SR,0,10.0,DAQmx_Val_GroupByChannel,out,NULL,NULL));

	printf("Press enter to begin experiment.\n");
	getchar();

	initAllegro();
	for(int nc=0;nc<NumChannels;nc++){
	zeroPoint[nc] = (graphWidth/2)*(2*nc+1)+spacingV*(nc+1);
	initScreen(nc);
	}

	cout <<"Please input a file name"<<endl;
    getline (cin, filename);
	filename += ".bin";

	printf("Press any key to begin data acquisition.\n");
	getchar();
	clear_keybuf();

	/*********************************************/
	// DAQmx Start Code
	/*********************************************/
	//DAQmxErrChk (DAQmxStartTask(AOtaskHandle));
	DAQmxErrChk (DAQmxStartTask(AItaskHandle));

	printf("Acquiring samples continuously.\n \
		   c: center trace about cumulative average\n \
		   z: center and zoom in on y axis.\n \
		   o: center and zoom out of y axis\n \
		   q: quit data acquisition\n");
	
	while(c != 'q'){

		if (c=='c') {
			
			while ((std::cout << "Type channel number you want to center\n") && !(std::cin >> chan) && !inCallBack) {
					std::cin.clear();
					std::cin.ignore(std::numeric_limits<std::streamsize>::max(), '\n');
					std::cout << "That's not an active channel number";
			}
			
			if(!inCallBack){
				printf("Centering channel %d. \n",chan);
				rescaleRequested = true;
			}

		} else if (c=='z') {

			while ((std::cout << "Type channel number you want to center\n") && !(std::cin >> chan) && !inCallBack) {
					std::cin.clear();
					std::cin.ignore(std::numeric_limits<std::streamsize>::max(), '\n');
					std::cout << "That's not an active channel number";
			}

			if(!inCallBack){
				printf("Zooming in on Y-axis of chan %d. \n", chan);
				scaleV[chan] = scaleV[chan]/0.5;
				rescaleRequested = true;
			}
			
		} else if (c=='o') {

			while ((std::cout << "Type channel number you want to center\n") && !(std::cin >> chan) && !inCallBack) {
					std::cin.clear();
					std::cin.ignore(std::numeric_limits<std::streamsize>::max(), '\n');
					std::cout << "That's not an active channel number";
			}

			if(!inCallBack){
			printf("Zooming out of Y-axis of chan %d. \n", chan);
			scaleV[chan] = scaleV[chan]*0.5;
			rescaleRequested = true;
			}
			
		} else {
			c = '\0';
		}

		fflush(stdin);
		c = '\0';
	
		if (!inCallBack) c = getchar();
	}

	printf("End of program, wait for tasks to close.\n");
	getchar();

Error:
	if( DAQmxFailed(error) )
		DAQmxGetExtendedErrorInfo(errBuff,2048);
	if( AItaskHandle!=0 ) {
		/*********************************************/
		// DAQmx Stop Code
		/*********************************************/
		DAQmxStopTask(AItaskHandle);
		DAQmxClearTask(AItaskHandle);
	}
	//if( DAQmxFailed(error) )
	//	printf("DAQmx Error: %s\n",errBuff);
	//if( AOtaskHandle!=0 ) {
	//	/*********************************************/
	//	// DAQmx Stop Code
	//	/*********************************************/
	//	DAQmxErrChk (DAQmxWriteAnalogF64(AOtaskHandle,1,1,10.0,DAQmx_Val_GroupByChannel,zero,NULL,NULL));
	//	DAQmxStopTask(AOtaskHandle);
	//	DAQmxClearTask(AOtaskHandle);
	//}
	printf("Tasks stopped. Press Enter key to close the program.\n");
	getchar();
	return 0;
}
int32 CVICALLBACK EveryNCallback(TaskHandle taskHandle, int32 everyNsamplesEventType, uInt32 nSamples, void *callbackData)
{
	//printf("in call back\n");
	inCallBack = true;
	int32       error=0;
	char        errBuff[2048]={'\0'};
	static int  totalRead=0;
	int32       read=0;
	int16		data[2*SAMPS_PER_CHAN_PER_CALLBACK*NumChannels];

	int16		n = 0;
	uint16_t	temp = 0;
	int			nc = 0;
	int			dec=0;
	bool		nIsNeg = false;
	int			nPointAvg = 20;
	int			j = 0;

	/*********************************************/
	// DAQmx Read Code
	/*********************************************/
	DAQmxErrChk (DAQmxReadBinaryI16(taskHandle,SAMPS_PER_CHAN_PER_CALLBACK,10.0,DAQmx_Val_GroupByScanNumber,data,2*SAMPS_PER_CHAN_PER_CALLBACK*NumChannels,&read,NULL));

	if(read>0) {
		pFile = fopen(filename.c_str(), "ab");
		fwrite (data, sizeof(char), 2*SAMPS_PER_CHAN_PER_CALLBACK*NumChannels, pFile); 
		fclose (pFile);
		fflush(stdout);

		for(nc=0;nc<NumChannels;nc++){
			dec = 0;
			for(j=0;j<nPointAvg;j++){	
			n = data[nc+(NumChannels*SR/nPointAvg)*j];
			temp = (unsigned int) n>>15;
			if (temp > 1){
				n = ~n;
				n--;
				nIsNeg = true;
			}

			for(double i=0; n != 0; i++){
					if(n % 2 == 1) {
						dec += pow(2, i);
					}
					n /= 2;
				}
			}

			if (nIsNeg) dec = dec*(-1);
			nIsNeg = false;
			displayedValues[nc][displayUpdateNumber] = (float) dec*(MAX-MIN)/65536/nPointAvg;

			cumulativeSum[nc] += displayedValues[nc][displayUpdateNumber];
			printf("Acquired %d samples. Total %d. Current value on channel 0 - %f \r",read,totalRead+=read,displayedValues[0][displayUpdateNumber]);
			
			if (rescaleRequested){
				centerTrace(chan);
				initScreen(chan);
				ccol = col;
				redrawTrace(chan,ccol);
				rescaleRequested = false;										// clear rescale request flag
			}
			updateDisplay(nc);
		}
		displayUpdateNumber++;

		if(col<COL-spacingH){
			col++;
		} else {
		clear_to_color(bmp,makecol(200,200,200));
		clear_to_color(screen,makecol(200,200,200));
		for (int nc=0;nc<NumChannels;nc++) initScreen(nc);
		col = spacingH+1;
		screenCycles++;
		}

	}

Error:
	if( DAQmxFailed(error) ) {
		DAQmxGetExtendedErrorInfo(errBuff,2048);
		/*********************************************/
		// DAQmx Stop Code
		/*********************************************/
		DAQmxStopTask(taskHandle);
		DAQmxClearTask(taskHandle);
		printf("DAQmx Error: %s\n",errBuff);
	}

	inCallBack = false;
	return 0;
}
int32 CVICALLBACK DoneCallback(TaskHandle taskHandle, int32 status, void *callbackData)
{
	int32   error=0;
	char    errBuff[2048]={'\0'};

	// Check to see if an error stopped the task.
	DAQmxErrChk (status);

Error:
	if( DAQmxFailed(error) ) {
		DAQmxGetExtendedErrorInfo(errBuff,2048);
		DAQmxClearTask(taskHandle);
		printf("DAQmx Error: %s\n",errBuff);
	}
	return 0;
}
void initAllegro(){
	allegro_init();
	install_keyboard();
	set_color_depth(32);
	set_gfx_mode(GFX_AUTODETECT_WINDOWED,COL,ROW,0,0);
	set_display_switch_mode(SWITCH_BACKGROUND);
	get_palette(pal);
	bmp=create_bitmap(COL,ROW);
}
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

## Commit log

2017-10-30 added BOM
    [BOM.xlsx]
2017-10-30 updated bom
    [BOM.xlsx]
2017-11-30 added electronics and optics documentation
    [AC127-019-A-Solidworks.sldprt, AC254-040-A-Solidworks.sldprt, AD12F-Solidworks.sldprt, B1C-Solidworks.sldprt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]
2017-11-30 changed filetype of assembly instructions
2017-12-05 pmt hv supply docs and bom update
    [BOM.xlsx, hvsupply_schem.SchDoc]
2017-12-05 hv supply assembly instructions
2017-12-11 changes to optical system 3d model, new tests added to assembly instructions, changes to bom
    [BOM.xlsx, LM1XY-Solidworks.sldprt, ND504B-Solidworks.sldprt, SM1T2-Solidworks.sldprt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]
2017-12-13 changed daq in bom
    [BOM.xlsx]
2017-12-13 reverted 6351 daq in bom
    [BOM.xlsx]
2017-12-14 thorlabs parts costs to usd
    [BOM.xlsx]
2018-03-14 reorganized files into ciclops-core and features folders
    [AC127-019-A-Solidworks.sldprt, AC254-040-A-Solidworks.sldprt, AD12F-Solidworks.sldprt, B1C-Solidworks.sldprt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]
2018-03-14 removed experimental features
    [KEMET Electronics Footprints.PcbLib, LIA_slave.PcbDoc, LIA_slave.PrjPCB, LIA_slave.SchDoc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]
2018-03-15 moved high voltage power supply to optics
    [hvsupply_schem.SchDoc]
2018-03-15 alternate product for deprecated filter
    [BOM.xlsx]
